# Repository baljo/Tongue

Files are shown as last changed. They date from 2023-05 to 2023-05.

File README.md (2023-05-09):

# Thomas' Tongue

# Introduction

Inspired by how Benjamin Cabé's amazing [artificial nose](https://blog.benjamin-cabe.com/2021/08/03/how-i-built-a-connected-artificial-nose) can recognize different scents, I thought it would be interesting to find out if it was possible to simulate the tastebuds of a human tongue to detect different types of - more or less - drinkable liquids. This tutorial shows how low-cost water quality sensors, together with WIO Terminal, were used to successfully detect five different liquids with help of TinyML (Tiny Machine Learning).
  


# Use-case Explanation

This project belongs mainly to basic research and thus I don't have a real problem to solve. However, many ideas have popped up for how the learnings from this project could be taken further for real use:
- Use in olfactory (smell and taste) training for patients suffering from loss of smell and taste (see *below)
- Use in wine tasting, for this an additional pH sensor is probably needed
- Use in water quality verification, e.g. for waste water treatment 

**A lot of people are unfortunately suffering from partial or complete anosmia (loss of smell) and ageusia (loss of taste). The reasons for the loss vary, but especially during the last few years Covid-19 has been recoqnized as one significant contributor. While most of the people having suffered through Covid-19 or other respitarory illnesses eventually fully recover their taste and smell capabilities, [one study](https://www.bmj.com/company/newsroom/millions-of-covid-patients-may-have-long-term-smell-and-taste-problems/#:~:text=They%20found%20that%20smell%20loss,of%20patients%20reported%20taste%20recovery) reports that approximately 5 % of patients having recovered from Covid-19 have a persisting loss of smell and/or taste a long time after.*

## Sensors Used in this Project

The two sensors that are used in this project are (see next chapter for further links):
- Grove TDS Sensor
- Grove Turbidity Sensor

**What is TDS and why should you care**

TDS = Total Dissolved Solids, is a measure of the dissolved combined content of all inorganic and organic substances present in water. Typically, the higher the TDS value, the more substances dissolved in water. Hence, higher levels of Total Dissolved Solids (TDS) can indicate that water has more contaminants that can pose health risks. *(Source [Seeedstudio](https://www.seeedstudio.com/Grove-TDS-Sensor-p-4400.html?queryID=8b51e6082631abe27d9dc97a983936bc&objectID=4400&indexName=bazaar_retailer_products))*

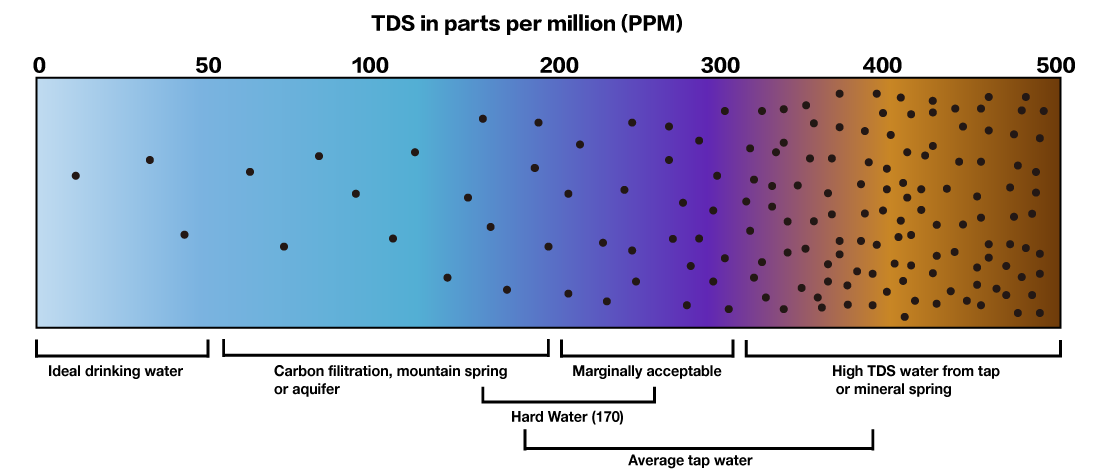
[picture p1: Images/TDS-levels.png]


**What is turbidity**

The Grove turbidity sensor can measure the turbidity of the water (the number of suspended particles).

The optical sensor of this module can measure the density of turbid water and the concentration of extraneous matter using the refraction of wavelength between photo transistor and diode. By using an optical transistor and optical diodes, an optical sensor measures the amount of light coming from the source of the light to the light receiver, in order to calculate turbidity of water. *(Source [Seeedstudio](https://wiki.seeedstudio.com/Grove-Turbidity-Sensor-Meter-for-Arduino-V1.0/))*

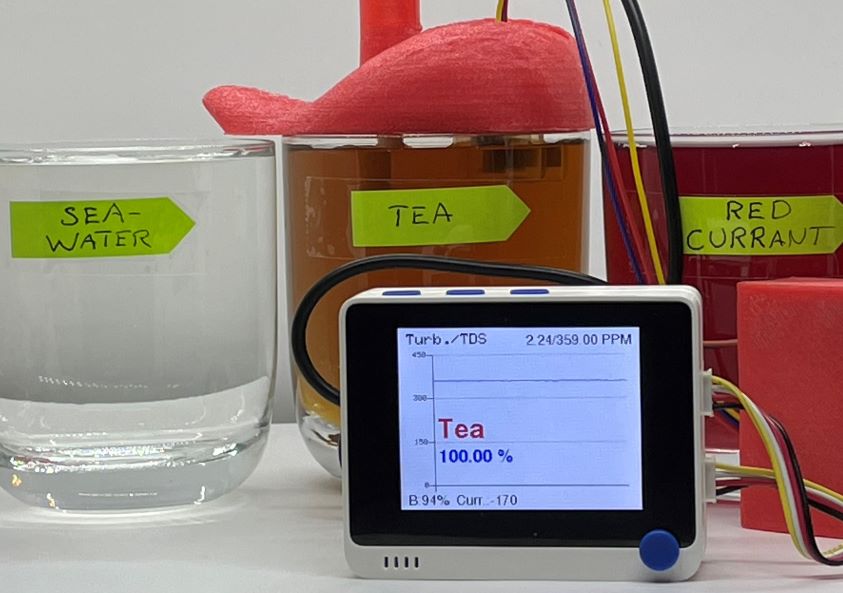
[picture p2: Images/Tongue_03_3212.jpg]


# Components and Hardware Configuration

## Components

### Required
- [Wio Terminal](https://www.seeedstudio.com/Wio-Terminal-p-4509.html?queryID=9771732d93468a0f30dbfc5262e76c34&objectID=4509&indexName=bazaar_retailer_products), SKU 102991299
- [Grove - TDS Sensor/Meter For Water Quality](https://www.seeedstudio.com/Grove-TDS-Sensor-p-4400.html?queryID=4a630ba8b2d70bcfca1375237f32fc0d&objectID=4400&indexName=bazaar_retailer_products), SKU 101020753
- [Grove - Turbidity Sensor](https://www.seeedstudio.com/Grove-Turbidity-Sensor-p-4399.html?queryID=83279b52ae522a495d8f87efd2c3784c&objectID=4399&indexName=bazaar_retailer_products), SKU 101020752

### Optional but Recommended
- [Wio Terminal Chassis - Battery (650mAh)](https://www.seeedstudio.com/Wio-Terminal-Chassis-Battery-650mAh-p-4756.html?queryID=2b0ff4e58b77c003e5bc9e13352a3459&objectID=4756&indexName=bazaar_retailer_products), SKU 103990564
- 3D-printer to print tongue and case 
    - While PETG- or PLA-filaments also work, TPU-filament is recommended due to its softness and flexibility. For example, the case and the lid for the PCB boards fits perfectly together as they can be squeezed a bit when attaching to each other.
    - If you don't want to 3D-print a case for the PCB boards, at least put them in separate match boxes or similar to minimize the risk of liquids dropping on them. Electronics and liquids don't play well together...
    - The Turbidity sensor has holes on the top, so it's not water tight = do not immerse it completely in liquids. By a 3D-printed tongue, or by your own sensor case design, the sensors can be held at proper depth and thus minimizing the risk that the turbidity sensor breaks due to liquids inside it. Make it almost fool-proof by also putting hot glue or adhesive putty (Blu tack) on the holes.

## Hardware Configuration
- Put the PCB boards into the 3D-printed case first
- Connect the cable for the TDS-sensor to Grove port A2, and the cable for the Turbidity sensor to Grove port A4 on the battery chassis
    - you can of course use any other analog port as long as you change the relevant defines in the code (`#define TDS_Pin A2` and 
`#define turbidity_Pin A4`). If not using Grove ports or the battery chassis, you can use the 40-Pin GPIO Header at the back.
- Double-check the connections

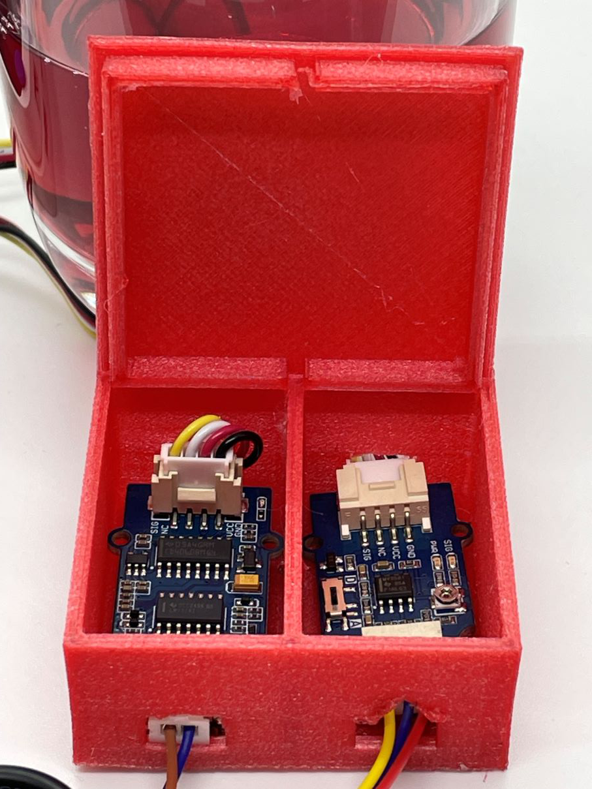
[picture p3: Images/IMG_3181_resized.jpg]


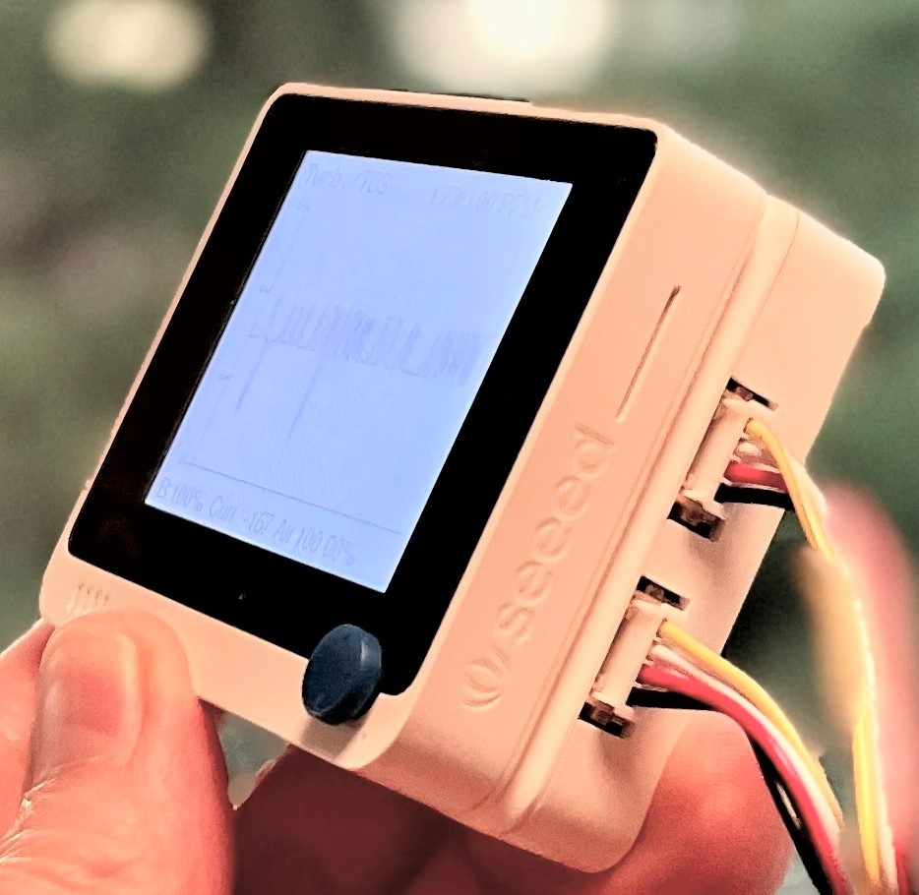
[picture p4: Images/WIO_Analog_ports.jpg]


### 3D-printing the Tongue and the PCB Case
- The different STL-files are found at the [GitHub repository](https://github.com/baljo/Tongue/tree/main/3D%20Model/STL-files)
    - [PCB case](https://github.com/baljo/Tongue/blob/main/3D%20Model/STL-files/PCB%20case.stl)
    - [PCB lid](https://github.com/baljo/Tongue/blob/main/3D%20Model/STL-files/PCB%20lid.stl)
    - [Tongue top](https://github.com/baljo/Tongue/blob/main/3D%20Model/STL-files/Tongue_top.stl)
    - [Tongue bottom](https://github.com/baljo/Tongue/blob/main/3D%20Model/STL-files/Tongue_bottom.stl)
- I used TPU-filament (from CCTree) for the first time and was surprised that it worked without issues on my budget Bowden-tube equipped 3D-printer. I did though not dare to go full speed (100 mm/s), instead used a moderate 50 mm/s, and a temperature of 220 °C. Print with high quality, I chose the max quality of 100 microns (0.1 mm), which made the printer working for hours with each part. 
- No support is needed, a brim or raft is though recommended. TPU-filament sticks better to the print bed than PLA, so a heated bed is probably not necessary, my printer is anyhow not having one.
- The "tongue" is split in two parts, the bottom part is not strictly needed, but provides some protection when the equipment is not in use, and makes it look more like a real tongue! If you are printing with very flexible TPU-material, you might want to make the bottom part a tad thicker than in the design files.

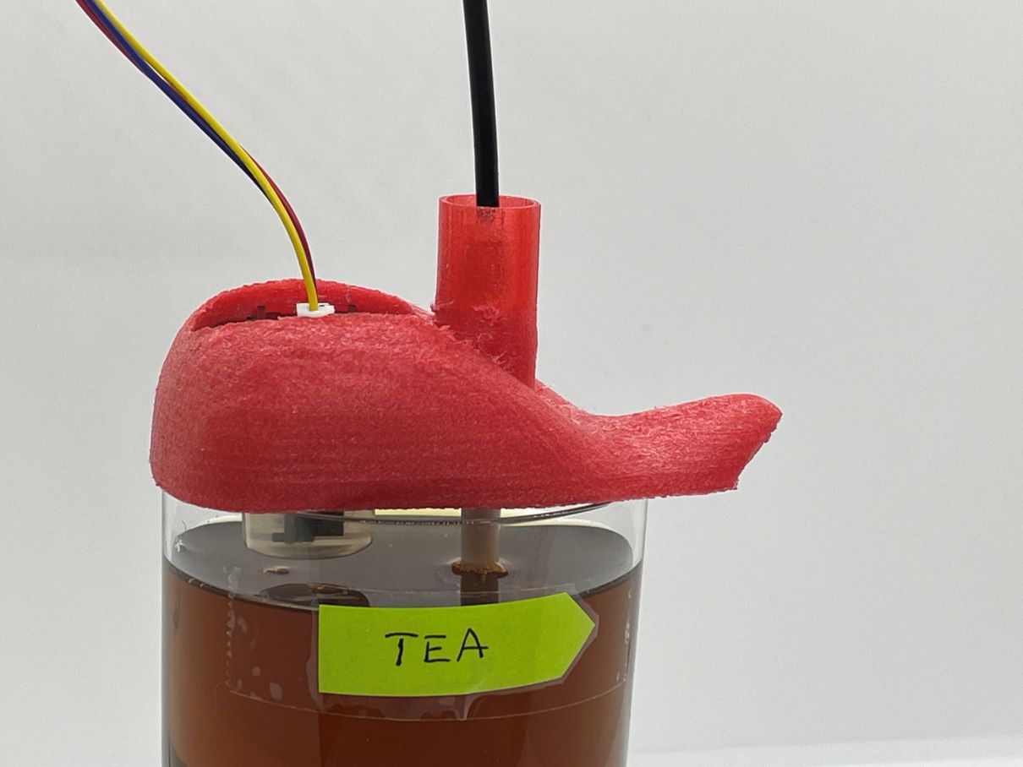
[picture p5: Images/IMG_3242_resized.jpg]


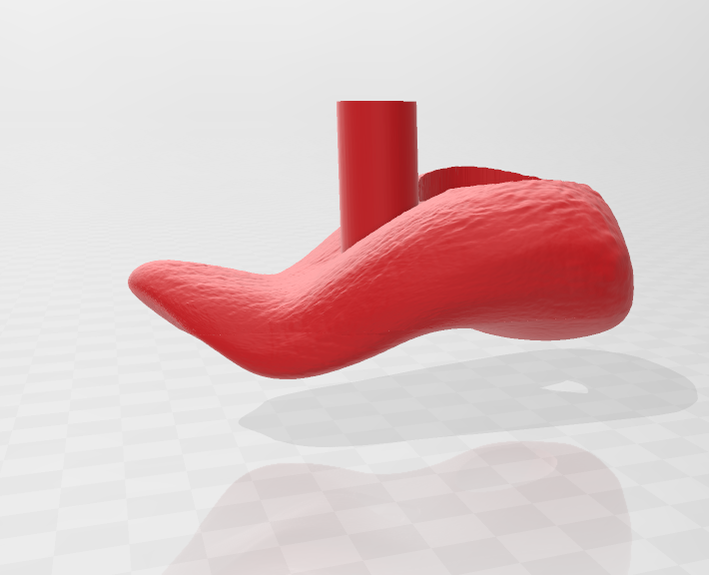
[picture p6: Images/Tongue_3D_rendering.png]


## Installing Software
To be able to gather data, and later to test the setup in practice, you need to prepare the WIO Terminal:
- Follow the steps in this [tutorial](https://wiki.seeedstudio.com/Wio-Terminal-TinyML-EI-1/)
- Add following libraries through the Arduino IDE via `Sketch > Include Library > Add .ZIP library`:
    - [ei-tongue-arduino-1.0.2.zip](https://github.com/baljo/Tongue/blob/main/ei-tongue-arduino-1.0.2.zip)
    - If using the battery chassis, and you want to see the battery status: [SparkFun BQ27441-G1A LiPo Fuel Gauge Arduino Library](https://github.com/sparkfun/SparkFun_BQ27441_Arduino_Library/tree/master) 
    - Visit [Seeed_Arduino_Linechart](https://github.com/Seeed-Studio/Seeed_Arduino_Linechart) and download the entire repo to your local drive. Then add the .ZIP-file as above

# Data Collection Process

To collect data using Edge Impulse, there's only a few steps to take:

**Preparations**
- Find at least two liquids, e.g. tap water and sea water. Do not use any liquids that might damage the sensors like oil, acids, or very corrosive liquids. 
    - After you have immersed the sensors in a liquid, rinse them carefully with water and wipe them dry. 
- Compile and upload the main program [Tongue.ino](https://github.com/baljo/Tongue/blob/main/Tongue.ino) to your WIO Terminal
    - This program is used both for collecting data, and later for inferencing. The program writes sensor data to the terminal which will be collected by the data forwarder in next step.
- Use the Edge Impulse [data forwarder](https://docs.edgeimpulse.com/docs/edge-impulse-cli/cli-data-forwarder), force the frequency to be 5 Hz by `edge-impulse-data-forwarder --frequency 5`
    - When you see this message `2 sensor axes detected (example values: [3,1.79]). What do you want to call them? Separate the
 names with ',':`, type `TDS, Turbidity` as these are the sensor labels used in the program.
    - More info about how the data forwarder works can be found [here](https://docs.edgeimpulse.com/docs/edge-impulse-cli/cli-data-forwarder).

**Collect Data**
- Head over to Edge Impulse, create a project if not already done so, and go to `Data acquisition`
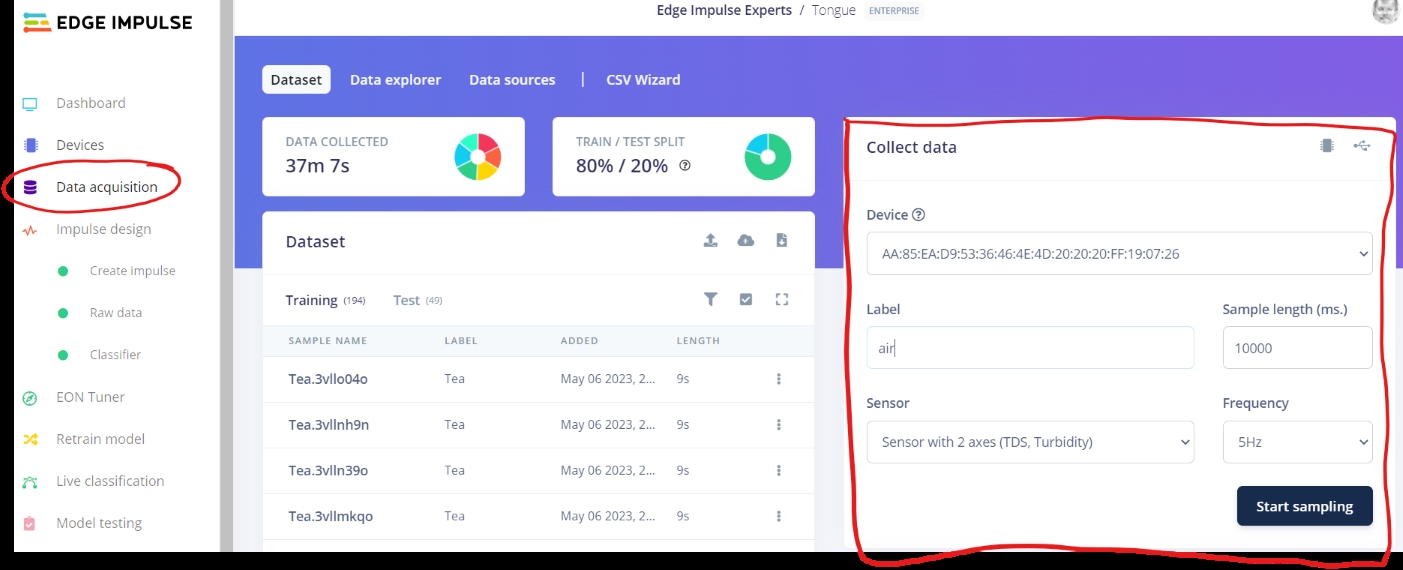
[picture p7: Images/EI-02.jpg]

- Your device should now be visible on the right side.
- Use a sample length of 10000 ms (= 10 seconds), the frequency is automatically 5 Hz as you forced it to be in the preparation steps.
- The first label you should record data for is `air` that is, do not immerse the sensors in any liquid, just keep them in the air.
    - It is often necessary to have a label that serves as *other* or *background*. In this case the label `air` is even "hard coded" in the program, but the program will technically work fine even if you don't use `air` as label.
- Click on `Start sampling` to collect data, I collected roughly 6 minutes of data for each label, but I recommend you start with a minute or so for each label. Machine learning is most often an iterative process, so start small and adjust if needed.
- When collecting data from liquids, ensure the sensors are immersed deep enough.
    - Check the animation in the beginning of this tutorial, the liquids are very close to the glass rims.
    - Name the liquids, preferably with a shortish label as they will be displayed on the WIO Terminal later.
    - Try to collect roughly same amount of data for each liquid.

**Important**
- You want to put aside some of the data samples as test data that will be used later. Depending on how you are collecting data, this will happen automatically or not. If the pie chart at the top shows 100%/0% as Train/Test split, you'll need to manually intervene. One way is to separately click on `Test` in the `Dataset` section and collect data there, but especially the first time it is easier to select ´Dashboard`, scroll down and then click `Perform train/test split`. This will create an ideal split of 80%/20%.

# Training and Building the Model

After collecting some data you are now ready to build and train a ML model:

**Create an Impulse and Generate Features**
- Select `Create impulse` from the menu, set the Window size to 2000 ms, Window increase to 500 ms, and frequency to 5 Hz.
- Select `Raw Data` as `Processing block` and `Classification` as `Learning block`
- Click `Save impulse`

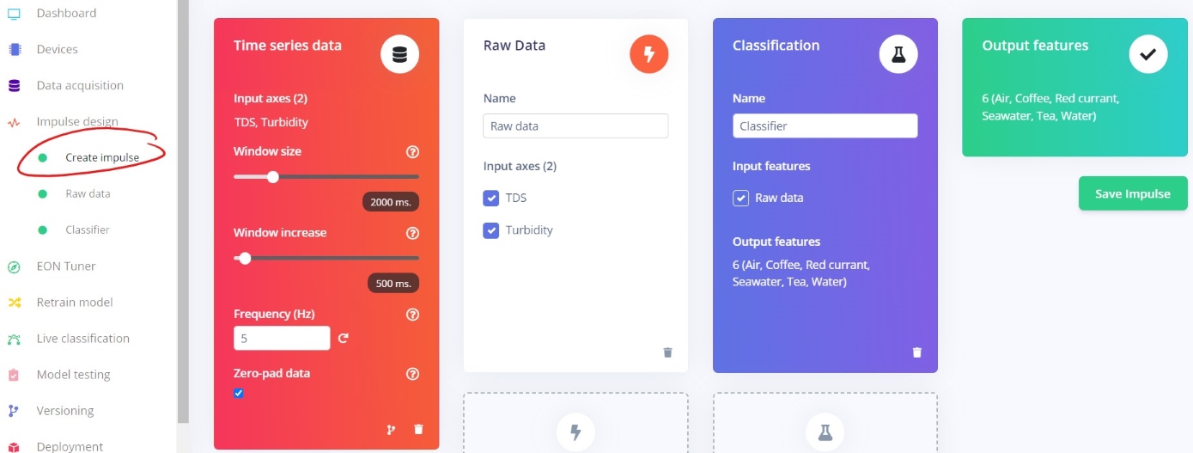
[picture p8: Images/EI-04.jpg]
    

- Select `Raw data` from the menu
- Click `Generate features`
    - After a while you'll see a graphical representation in the Feature explorer at the right. The more separated the classes are, the easier it will be for the model to classify. In this case the exact same liquid concentrations were used for each sample, this explains the nice separations. In most real cases though, the concentrations will to some degree vary from time to time, e.g. you probably never manage to brew tea with exactly same strength every time.

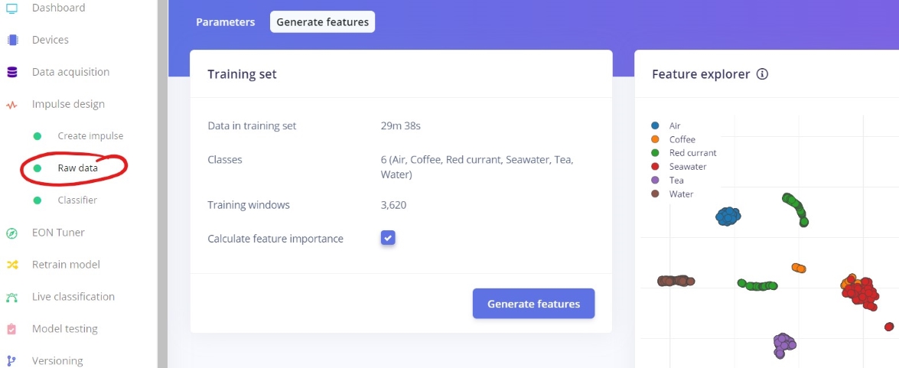
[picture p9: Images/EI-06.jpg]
    

**Train the Model**

- Select `Classifier` from the menu
- Change the settings as in the picture, most important changes are the Dense layers and the Dropout rate, but feel free to play around with other settings.
- The unoptimized float32 model will with these settings be very tiny, so there's no need to profile an quantized int8 model.
    - In my case the int8 accuracy has actually been extremely poor and useless, I haven't though investigated why, as the float32 model works just fine.
- Click on `Start training`, unless you have lots of data and/or a very huge neural network, the training will in this case take just a few minutes.
- Depending on your data quality/quantity and your model settings, you might or might not achieve a satisfying accuracy.
    - If you get a very poor accuracy with the unoptimized float32 model, you might need to collect more data, but in this case you should also check that the turbidity sensor (the wider one), really is immersed enough in the liquid, otherwise the optics might "see" only air.
    - After you have collected new data, click on `Retrain model`. This way you don't need to yourself generate new features.

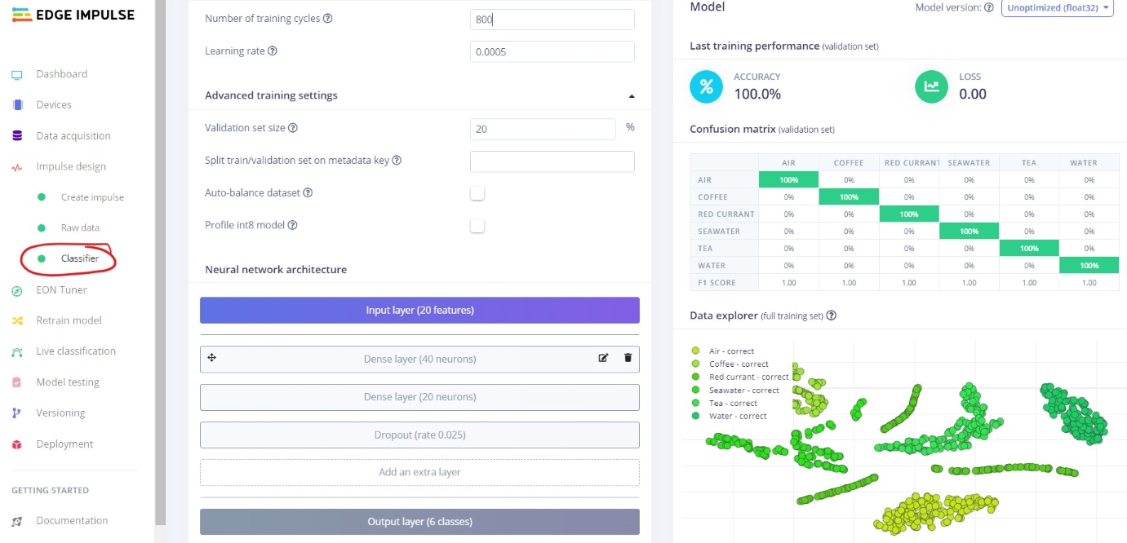
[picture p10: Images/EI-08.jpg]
    

**Test the Model**

For a dry test (literally dry in this case !), you will utilize test data that the ML model has not seen before. This will be as close to testing in real life as it can get.

- Select `Model testing` and click `Classify all`.
- Again you'll need to wait for a short while before seeing how the model performs on unseen data. Often the accuracy might be slightly worse than in the training phase, but sometimes it might even be better. The final truth will though be revealed first during wet testing.
- If the accuracy is much worse than in the training phase, the reason is often that the model is overfitting i.e., it models the training data too well and is not able to generalize.
    - In this case it might help to make the model less complex (reduce amount of neurons), increase the dropout rate, or if you have just a few data samples, collect more data.

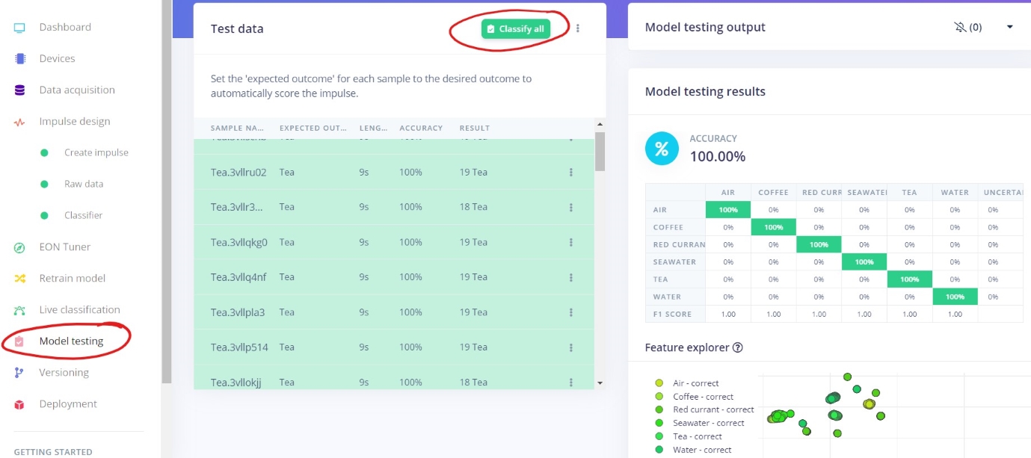
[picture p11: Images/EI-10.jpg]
    

# Model Deployment (Wet Testing)

When you are ready to test the model in real life, in this case with WIO Terminal, Edge Impulse has again made it very easy for you:

- Select `Deployment` from the menu
- Select `Arduino library`
- Select `Unoptimized (float32)`, and click `Build`

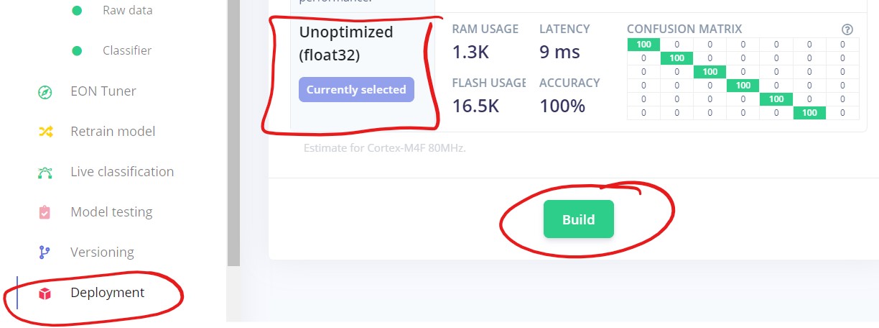
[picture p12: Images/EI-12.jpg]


- After a few minutes, a window will pop up, showing you how to include the Arduino library into your own code.
    - In this case, you should again open the file `Tongue.ino` in Arduino IDE, include the new library as instructed, and then replace `<Tongue_inferencing.h>` with your own library's header file. If you named your project e.g. `Liquids` in Edge Impulse, you'd put `<Liquids.h>` here.
```
/* Includes ---------------------------------------------------------------- */
#include <Tongue_inferencing.h> // <<===============--------------------------- REPLACE this with your own library's header file
#include <SparkFunBQ27441.h>   // to read battery info
#include "seeed_line_chart.h"  //include the line chart library
#include "TFT_eSPI.h"
```
- Finally compile and upload the program to WIO Terminal. 
    - If everything works you should on the device itself see a line chart with slightly varying data
    - The sensor data is also shown in the Arduino IDE terminal window

**Notes about the `Tongue.ino` program:**
- It finds the maximum classification value and takes that as the final prediction
- It is not using any uncertainty threshold i.e., it will classify everything it senses into one of the classes. Feel free to add uncertainty classification code into the Arduino program if you see a need for it, you only need to compare the classification value to a given uncertainty percentage threshold, e.g. 60 %.

# Results
The first results I got when testing the model in wet conditions were very mixed. Sometimes the model could always classify a liquid correctly, sometimes it completely failed. As I suspected I had not initially paid attention to having the turbidity sensor at proper and consistent depth, I started over from scratch by filling all glasses almost to the rims before data collection. This seems to have been the resolution to the problem as the model now works 100 % correctly. Again, this shows that machine learning as a paradigm is often an iterative process and it's better to start with a smaller amount of data, build and test a ML model, and then adjust if needed. 

As mentioned earlier, the quantized int8 model performs extremely poorly and is useless. This is interesting as the unoptimized float32 model has a 100 % accuracy both in theory as well as in practice. I've not investigated this further, but would be interested in learning why this huge discrepancy occurs, and how to correct it.

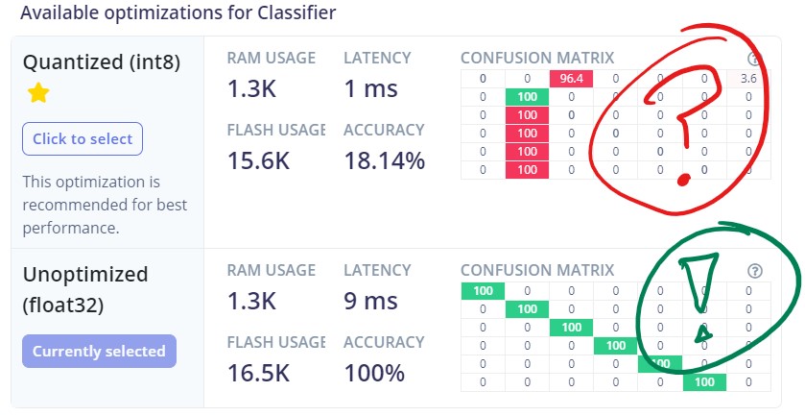
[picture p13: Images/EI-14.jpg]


In addition, I have not tested the model with different concentrations, and suspect it might struggle with very diluted liquids. To overcome this potential issue, one would need to collect data from liquids with different dilutations and retrain the model. Do also note that there most probably are completely different liquids that happen to have same characteristics as measured by the two sensors used. When both sensors measure similar values, even from completely different liquids, the liquids will from the model point of view be one and the same. This problem can be overcome by using "sensor fusion" that is, adding more or different type of sensors like e.g. gas sensors for scenting. With WIO Terminal and Grove-components this should actually be quite easy to do.

Despite above mentioned potential shortcomings, I was positively surprised that the model as such worked perfectly and consistently.

# Conclusion

In this project you've learned how to build a functioning ML project able to classify different liquids with a good or hopefully perfect accuracy. You are recommended to explore this more and take it a step further by adding more and different types of sensors, and especially try to find use cases where this type of technology can make a difference.



### *Attributions*

*The tongue 3D-design is an adaptation from this [3D-file](https://www.thingiverse.com/thing:644879) found at Thingiverse. All 3D-files I've created are licensed similarly as the original creator's (Attribution-ShareAlike 3.0 Unported/CC BY-SA 3.0).*

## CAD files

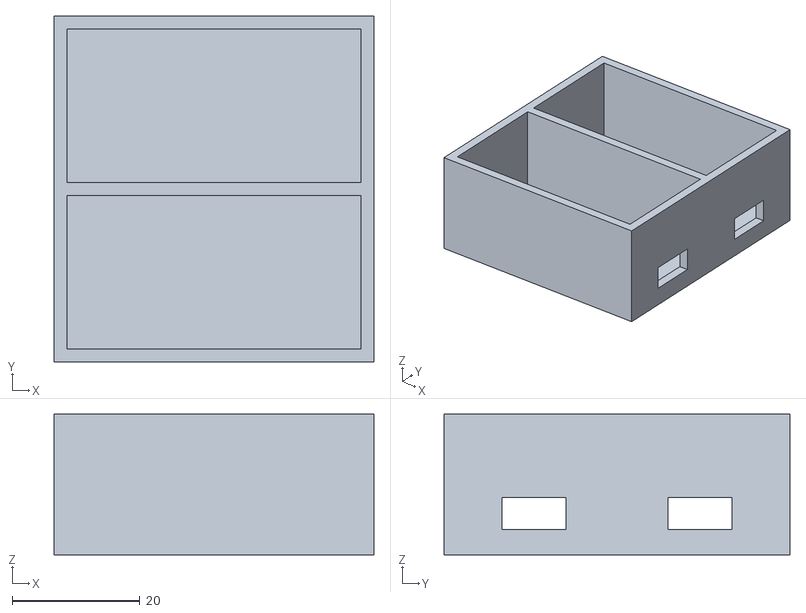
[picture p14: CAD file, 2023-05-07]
3D Model/Intermediate_3D-files/PCB case larger cable hole.stl
50.0 x 54.0 x 22.0

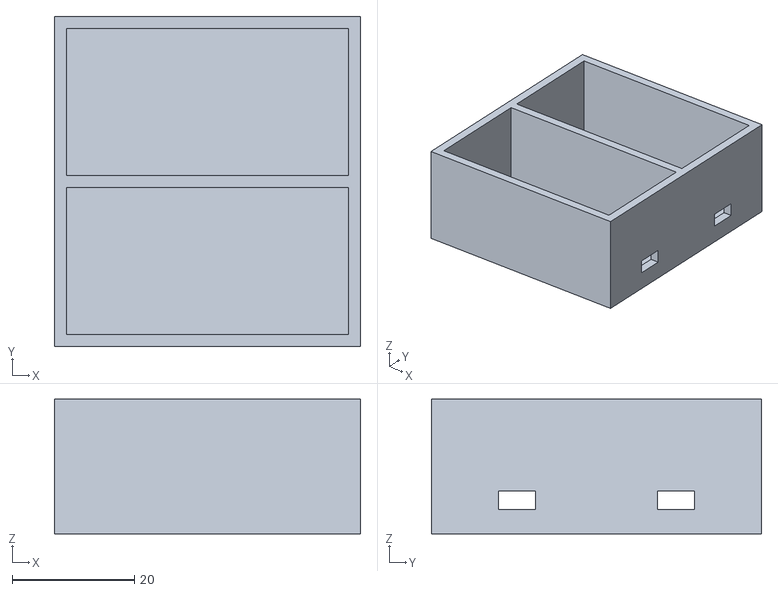
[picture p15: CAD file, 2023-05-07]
3D Model/STL-files/PCB case.stl
50.0 x 54.0 x 22.0

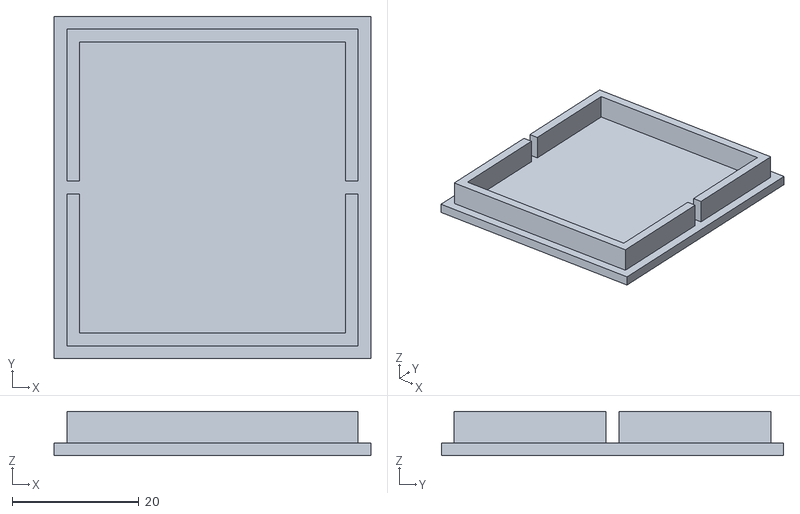
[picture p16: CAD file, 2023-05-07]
3D Model/STL-files/PCB lid.stl
50.0 x 54.0 x 7.00

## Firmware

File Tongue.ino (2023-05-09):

/* Edge Impulse ingestion SDK
 * Copyright (c) 2022 EdgeImpulse Inc.
 *
 * Licensed under the Apache License, Version 2.0 (the "License");
 * you may not use this file except in compliance with the License.
 * You may obtain a copy of the License at
 * http://www.apache.org/licenses/LICENSE-2.0
 *
 * Unless required by applicable law or agreed to in writing, software
 * distributed under the License is distributed on an "AS IS" BASIS,
 * WITHOUT WARRANTIES OR CONDITIONS OF ANY KIND, either express or implied.
 * See the License for the specific language governing permissions and
 * limitations under the License.
 *
 */

/* Includes ---------------------------------------------------------------- */
#include <Tongue_inferencing.h> // <<===============--------------------------- REPLACE this with your own library's header file
#include <SparkFunBQ27441.h>   // to read battery info
#include "seeed_line_chart.h"  //include the line chart library
#include "TFT_eSPI.h"

TFT_eSPI tft;


#define TDS_Pin A2
#define turbidity_Pin A4
#define MAX_SIZE 100  //maximum size of data
doubles stack[3];
TFT_eSprite spr = TFT_eSprite(&tft);  // Sprite
#define FF17 &FreeSans9pt7b
#define FF20 &FreeSans20pt7b
#define FF24 &FreeSans24pt7b
#define LCD_BACKLIGHT (72Ul)  // Control Pin of LCD

#define FREQUENCY_HZ 5
#define INTERVAL_MS (1000 / (FREQUENCY_HZ + 1))

float features[] = {
  0, 0, 0, 0, 0, 0, 0, 0, 0, 0, 0, 0, 0, 0, 0, 0, 0, 0, 0, 0
};
int i = 0;
int sensorValue = 0;
float tdsValue = 0;
float Voltage = 0;
char label[50] = "";

static unsigned long last_interval_ms = 0;

const unsigned int BATTERY_CAPACITY = 650;  // Set Wio Terminal Battery's Capacity


void setupBQ27441(void) {
  // Use lipo.begin() to initialize the BQ27441-G1A and confirm that it's
  // connected and communicating.
  if (!lipo.begin())  // begin() will return true if communication is successful
  {
    // If communication fails, print an error message and loop forever.
    Serial.println("Error: Unable to communicate with BQ27441.");
    Serial.println("  Check wiring and try again.");
    Serial.println("  (Battery must be plugged into Battery Babysitter!)");
    tft.setTextColor(TFT_RED);
    tft.setCursor((320 - tft.textWidth("Battery Not Initialised!")) / 2, 120);
    tft.print("Battery Not Initialised! ?");
    //while (1) ;
  }
  Serial.println("Connected to BQ27441!");

  // Uset lipo.setCapacity(BATTERY_CAPACITY) to set the design capacity
  // of your battery.
  lipo.setCapacity(BATTERY_CAPACITY);
}




/**
 * @brief      Copy raw feature data in out_ptr
 *             Function called by inference library
 *
 * @param[in]  offset   The offset
 * @param[in]  length   The length
 * @param      out_ptr  The out pointer
 *
 * @return     0
 */
int raw_feature_get_data(size_t offset, size_t length, float *out_ptr) {
  memcpy(out_ptr, features + offset, length * sizeof(float));
  return 0;
}

void print_inference_result(ei_impulse_result_t result);

/**
 * @brief      Arduino setup function
 */
void setup() {
  // put your setup code here, to run once:
  Serial.begin(115200);
  // comment out the below line to cancel the wait for USB connection (needed for native USB)
  //while (!Serial)
  ;
  Serial.println("Edge Impulse Inferencing Demo");

  tft.begin();
  tft.setRotation(3);
  spr.createSprite(TFT_HEIGHT, TFT_WIDTH);
  spr.setRotation(3);

  setupBQ27441();
}



/**
 * @brief      Arduino main function
 */
void loop() {

  sensorValue = analogRead(TDS_Pin);
  Voltage = sensorValue * 3.3 / 1024.0;                                                                     //Convert analog reading to Voltage
  tdsValue = (133.42 * Voltage * Voltage * Voltage - 255.86 * Voltage * Voltage + 857.39 * Voltage) * 0.5;  //Convert voltage value to TDS value
  tdsValue = round(tdsValue);

  int turbidityValue = analogRead(turbidity_Pin);        // read the input on analog pin 0:
  float turb_voltage = turbidityValue * (3.3 / 1024.0);  // Convert the analog reading (which goes from 0 - 1023) to a voltage (0 - 5V):
  unsigned int soc = lipo.soc();                         // Read state-of-charge (%)
  int current = lipo.current(AVG);                       // Read average current (mA)


  if (millis() > last_interval_ms + INTERVAL_MS) {
    last_interval_ms = millis();

    // by keeping the following rows you can use this program to both acquire data as well as for inferencing!
    Serial.print(tdsValue);
    Serial.print(",");
    Serial.println(turb_voltage);  // print out the value you read:

    if (i >= 19)
      i = 0;

    // filling the features array 
    features[i] = tdsValue;
    features[i + 1] = turb_voltage;

    i = i + 2;
  }


  if (sizeof(features) / sizeof(float) != EI_CLASSIFIER_DSP_INPUT_FRAME_SIZE) {
    ei_printf("The size of your 'features' array is not correct. Expected %lu items, but had %lu\n",
              EI_CLASSIFIER_DSP_INPUT_FRAME_SIZE, sizeof(features) / sizeof(float));
    delay(1000);
    return;
  }

  ei_impulse_result_t result = { 0 };

  // the features are stored into flash, and we don't want to load everything into RAM
  signal_t features_signal;
  features_signal.total_length = sizeof(features) / sizeof(features[0]);
  features_signal.get_data = &raw_feature_get_data;

  // invoke the impulse
  EI_IMPULSE_ERROR res = run_classifier(&features_signal, &result, false /* debug */);
  if (res != EI_IMPULSE_OK) {
    ei_printf("ERR: Failed to run classifier (%d)\n", res);
    return;
  }

  // below loop finds the maximum prediction score and uses that as the final prediction
  // you might also want to add a check for uncertainty if the highest score is e.g. < 60 %  
  float max = -1.0;
  for (uint16_t i = 0; i < EI_CLASSIFIER_LABEL_COUNT; i++) {
    if (result.classification[i].value > max) {
      max = result.classification[i].value;
      strncpy(label, ei_classifier_inferencing_categories[i], sizeof(label));
      label[0] = toupper(label[0]);
    }
    // uncomment these if you want to print the prediction to the terminal
    /*    ei_printf(" %s: ", label);
    ei_printf("%.5f\r\n", max);*/
  }


  if (stack[0].size() == MAX_SIZE) {
    for (uint8_t i = 0; i < 3; i++) {
      stack[i].pop();  //this is used to remove the first read variable
    }
  }
  stack[0].push(tdsValue);  //read variables and store in data
  stack[1].push(tdsValue);
  stack[2].push(tdsValue);

  draw_chart(turb_voltage, soc, current, max);

}


void draw_chart(float turb_voltage, unsigned int soc, int current, float max) {
  spr.fillSprite(TFT_WHITE);


  spr.setFreeFont(FF17);
  spr.setTextColor(TFT_BLACK);
  spr.drawString(String(turb_voltage) + "/" + String(round(tdsValue)) + " PPM", 170, 10);
  spr.drawString("B:" + String(soc) + "% " + " Curr.:" + String(current), 10, 220);

  int equal = strcmp(label, "Air");
  float prediction_perc = round(max * 100);

  if (equal == 0) {
    spr.drawString(label, 170, 220);
    spr.drawString(String(prediction_perc) + "%", 195, 220);
  } else {
    spr.setFreeFont(&FreeSansBold18pt7b);
    spr.setTextColor(TFT_RED);
    spr.drawString(label, 50, 120);
    spr.setFreeFont(&FreeSansBold12pt7b);
    spr.setTextColor(TFT_BLUE);
    spr.drawString(String(prediction_perc) + " %", 50, 160);
  }

  int y_low = 0;
  //Settings for the line graph title
  auto header = text(0, 0)
                  .value(" Turb./TDS")
                  .align(left)
                  .valign(vcenter)
                  .width(spr.width())
                  .thickness(2);

  header.height(header.font_height(&spr) * 2);
  header.draw(&spr);  // Header height is the twice the height of the font

  //  y_low = trunc(tdsValue / 4 * 3);
  y_low = 0.0;

  //Settings for the line graph
  auto content = line_chart(20, header.height());  //(x,y) where the line graph begins
  content
    .height(spr.height() - header.height() * 1.5)  //actual height of the line chart
    .width(spr.width() - content.x() * 2)          //actual width of the line chart
    .based_on(y_low)                               //Starting point of y-axis, must be a float
    .show_circle(false)                            //drawing a cirle at each point, default is on.
    .value({ stack[0], stack[1], stack[2] })       //passing through the data to line graph
    .max_size(MAX_SIZE)
    .color(TFT_BLUE, TFT_RED, TFT_BLUE)
    .backgroud(TFT_WHITE)
    .draw(&spr);

  spr.pushSprite(0, 0);
}


void print_inference_result(ei_impulse_result_t result) {

  /*  // Print how long it took to perform inference
  ei_printf("Timing: DSP %d ms, inference %d ms, anomaly %d ms\r\n",
            result.timing.dsp,
            result.timing.classification,
            result.timing.anomaly);
*/
  if (Serial) {
    ei_printf("Predictions:\r\n");
    for (uint16_t i = 0; i < EI_CLASSIFIER_LABEL_COUNT; i++) {
      ei_printf("  %s: ", ei_classifier_inferencing_categories[i]);
      ei_printf("%.5f\r\n", result.classification[i].value);
    }
  }
}
